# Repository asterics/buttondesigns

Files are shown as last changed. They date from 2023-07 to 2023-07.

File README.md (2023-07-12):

# Assistive Buttons

Depending on the use case and the abilities of a user, different button constructions might be useful.

In this folder, we share different button designs, which can be 3D printed.

## Arcade Buttons

These buttons are design around arcade buttons.

**Advantages:**
* Robust
* Cheap
* Easy to order

**Disadvantages:**
* Big button cases
* Relatively high actuation force necessary

**Use cases:**
* Spasticity
* No fine motor skills

**Necessary tools:**
* 3D Printer (or ordered 3D printed parts)
* Solder iron + solder
* Wirecutter
* (insulation stripping tool)

**Necessary parts:**
* 3D printed case
* 3.5mm stereo jack plug cable, jack to jack (you just need half of it for each button): [Example cable](https://www.aliexpress.com/item/4000208914309.html)
* Arcade button (24 or 30mm): [24mm](https://www.aliexpress.com/wholesale?SearchText=24mm+arcade+button) [30mm](https://www.aliexpress.com/wholesale?SearchText=24mm+arcade+button)

## Microswitches

We designed these switches for users with very low movements and little force to actuate buttons.
At Pollin, a German electronics distributor, we found ALPS keyboard switches with 0.3N actuation force, perfect for us!

In addition, the small case is designed to hold a 2.5mm² copper wire, which is used for flexible mounting of the button, as close
as possible to the user's fingers or toes.

**Advantages:**
* Very little force necessary
* Fast printing
* Flexible mounting
* Tiny

**Disadvantages:**
* Switches are more expensive
* Not that robust
* Switches are discontinued, but replacement is available

**Use cases:**
* Little movement possible
* Narrow space for button mounting
* Little actuation force necessary

**Necessary tools:**
* 3D printer (or ordered 3D printed parts)
* Solder iron + solder
* Wirecutter
* Hot glue gun + hot glue (or euqivalent glue, e.g. epoxy)

**Necessary parts:**
* 3D printed case
* 2.5mm²/AWG13 copper wire (~30cm/12") with insulation for mounting
* 3.5mm stereo jack plug cable, jack to jack (you just need half of it for each button): [Example cable](https://www.aliexpress.com/item/4000208914309.html)
* ALPS SPVF140100: [Pollin (Germany)](https://www.pollin.de/p/2-wege-eingabetaster-alps-spvf140100-420643) [Neuhold Elektronik (Austria)](https://www.neuhold-elektronik.at/catshop/product_info.php?products_id=4348) [Aliexpress](https://www.aliexpress.com/wholesale?SearchText=SPVF140100)

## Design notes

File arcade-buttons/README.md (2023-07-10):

These button designs are used for Arcade buttons. Depending on the ordered button diameter, please print either **button_24mm.stl** or **button_30mm.stl**.

Following parts are necessary (in addition to the 3D print):

* Arcade button (either 24mm or 30mm diameter)
* 3.5mm jack plug stereo audio cable (you can cut a plug-to-plug wire into half for 2 buttons)

After printing the case, you need to remove the built-in support material within the button.

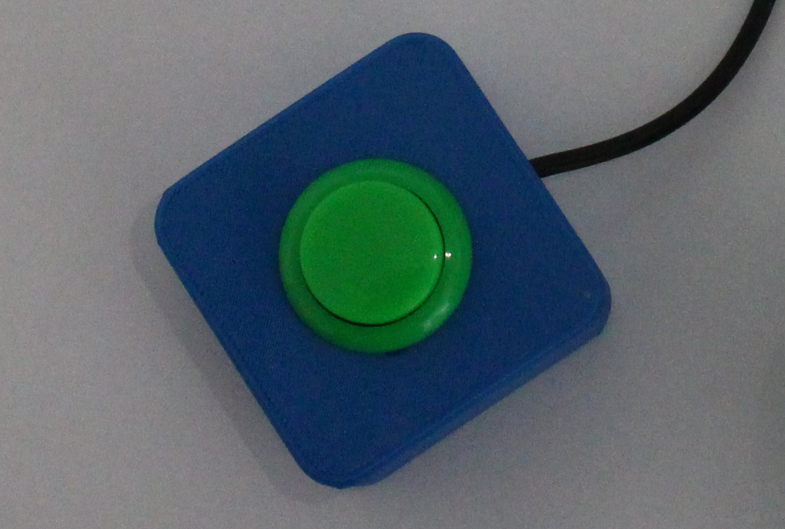
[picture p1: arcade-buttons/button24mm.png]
Image of a 24mm button

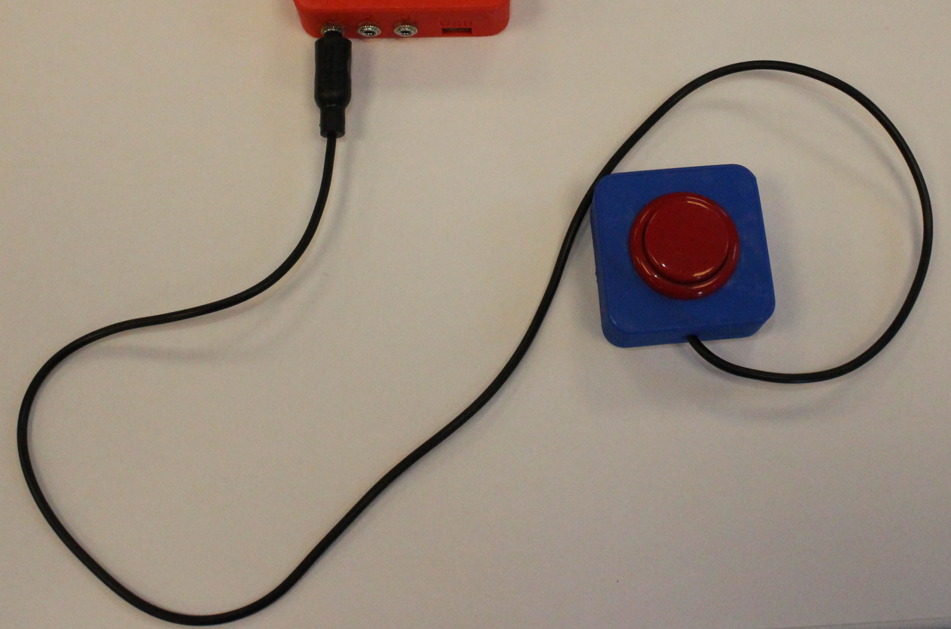
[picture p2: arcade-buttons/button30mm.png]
Image of a 30mm button


## Designfiles

Both button designs are located in __arcade_buttons.FCStd__ or __arcade_buttons_round.FCStd__ for the round case.

## Print settings & tools

All designs are made with FreeCAD v0.20.1.

Recommended print settings:

* 0.2-0.35mm
* Place the button hole on the printbed!
* No support
* Please use PLA or other biocompatible/-degradable filament (we use GreenTec from extrudr.at)

All designs are tested on a Prusa i3 MK3.

## Pictured construction manual

* [German](./ArcadeButton_DE.pdf?raw=true)
* [English](./ArcadeButton_EN.pdf?raw=true)

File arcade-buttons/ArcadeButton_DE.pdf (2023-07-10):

# Arcade Button – Bauanleitung

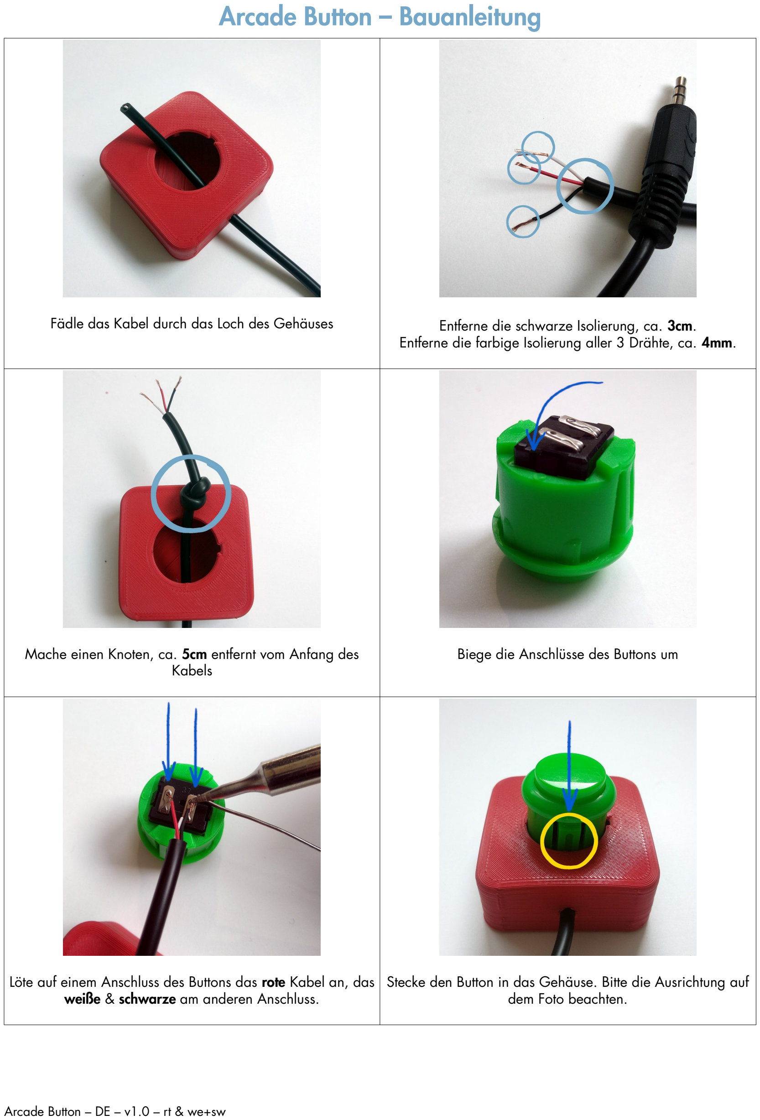
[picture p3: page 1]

Fädle das Kabel durch das Loch des Gehäuses | Entferne die schwarze Isolierung, ca. 3cm. Entferne die farbige Isolierung aller 3 Drähte, ca. 4mm.
Mache einen Knoten, ca. 5cm entfernt vom Anfang des Kabels | Biege die Anschlüsse des Buttons um
Löte auf einem Anschluss des Buttons das rote Kabel an, das weiße & schwarze am anderen Anschluss. | Stecke den Button in das Gehäuse. Bitte die Ausrichtung auf dem Foto beachten.

Arcade Button – DE – v1.0 – rt & we+sw

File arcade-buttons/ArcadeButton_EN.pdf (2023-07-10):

# Arcade Button – Construction Manual

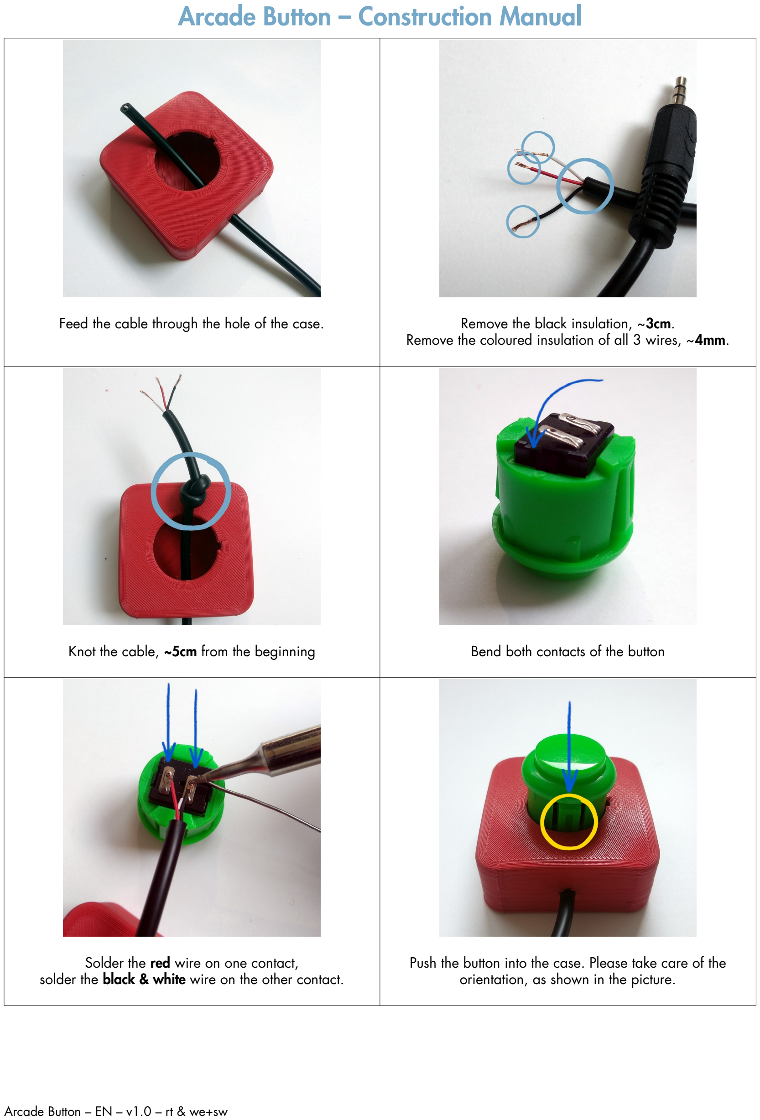
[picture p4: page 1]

Feed the cable through the hole of the case. | Remove the black insulation, ~3cm. Remove the coloured insulation of all 3 wires, ~4mm.
Knot the cable, ~5cm from the beginning | Bend both contacts of the button
Solder the red wire on one contact, solder the black & white wire on the other contact. | Push the button into the case. Please take care of the orientation, as shown in the picture.

Arcade Button – EN – v1.0 – rt & we+sw

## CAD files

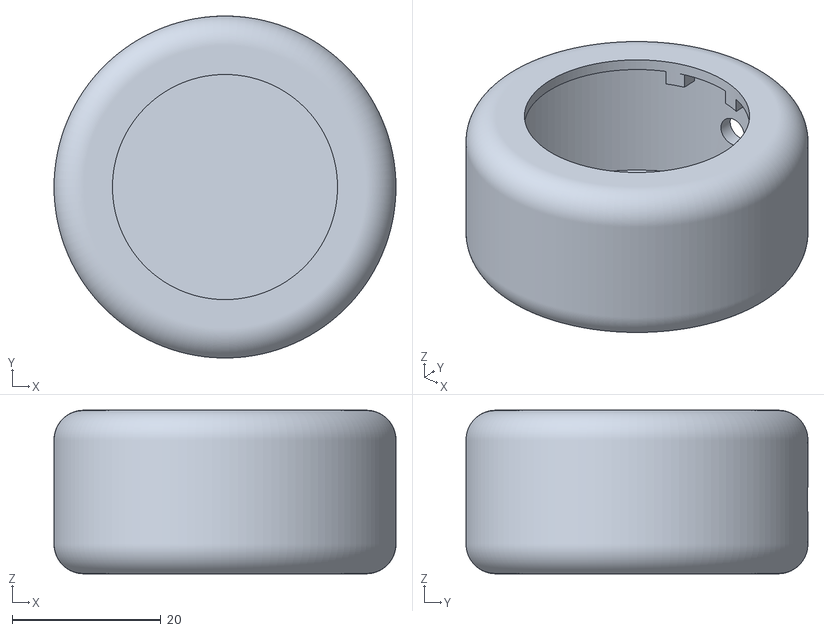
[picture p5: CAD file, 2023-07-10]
arcade-buttons/round_30mm.stl
46.0 x 46.0 x 22.0

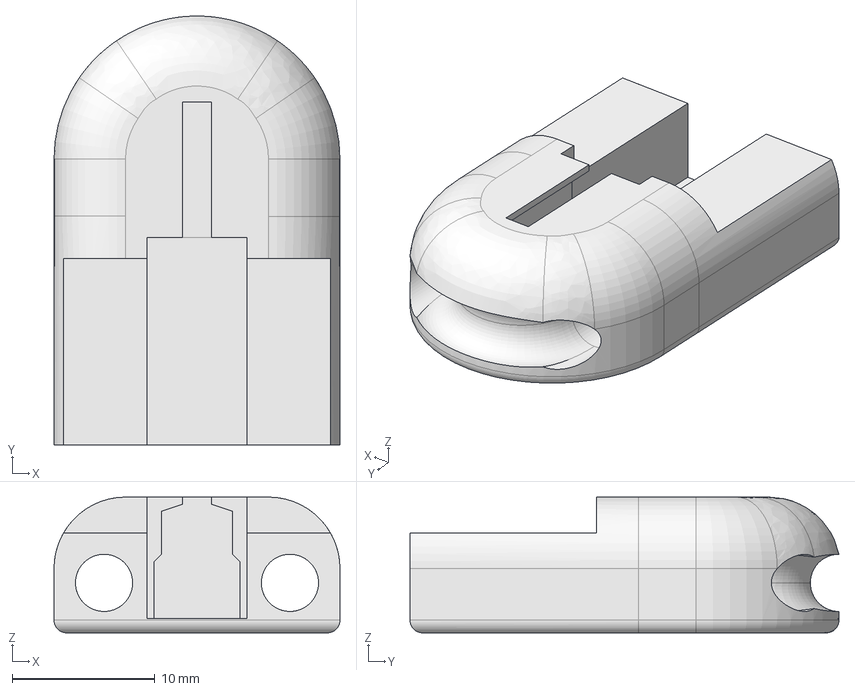
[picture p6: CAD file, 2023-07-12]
microswitch/ALPS_button.fcstd
20.0 x 30.0 x 9.50 mm

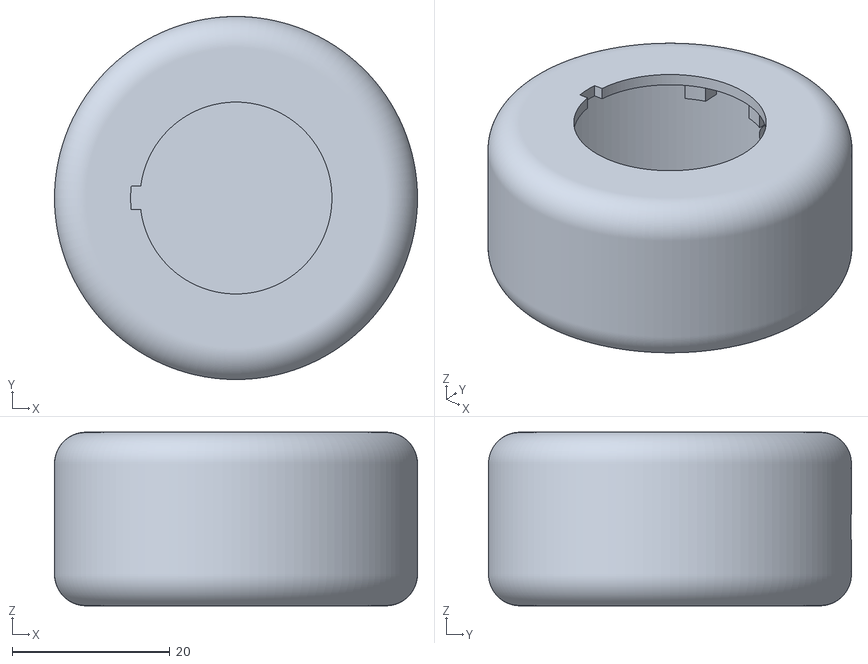
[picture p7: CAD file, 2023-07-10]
arcade-buttons/round_24mm.stl
46.0 x 46.0 x 22.0

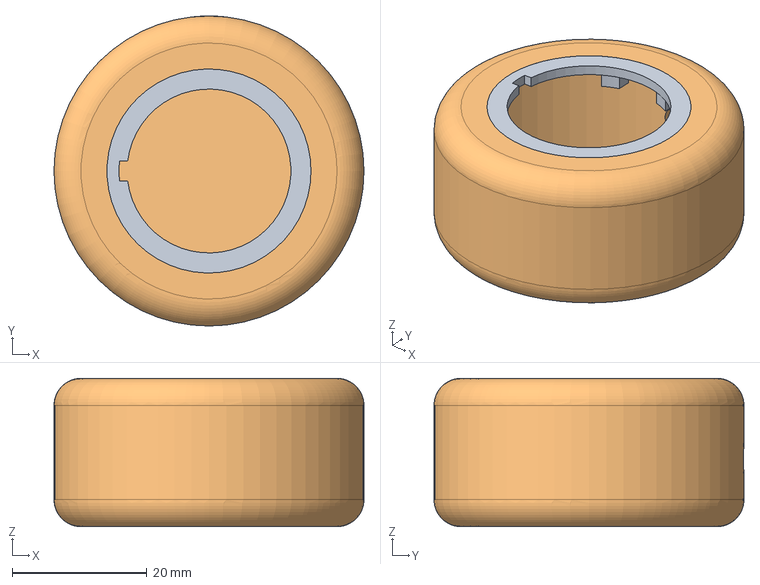
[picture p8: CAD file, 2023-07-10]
arcade-buttons/arcade_buttons_round.FCStd
46.0 x 46.0 x 22.0 mm
case_24mm
case_30mm

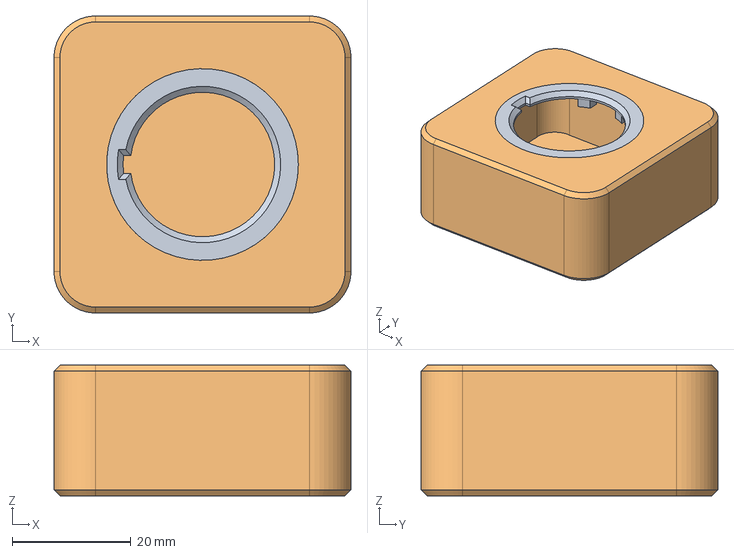
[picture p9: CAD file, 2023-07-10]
arcade-buttons/arcade_buttons.FCStd
50.0 x 50.0 x 22.0 mm
case_24mm
case_30mm

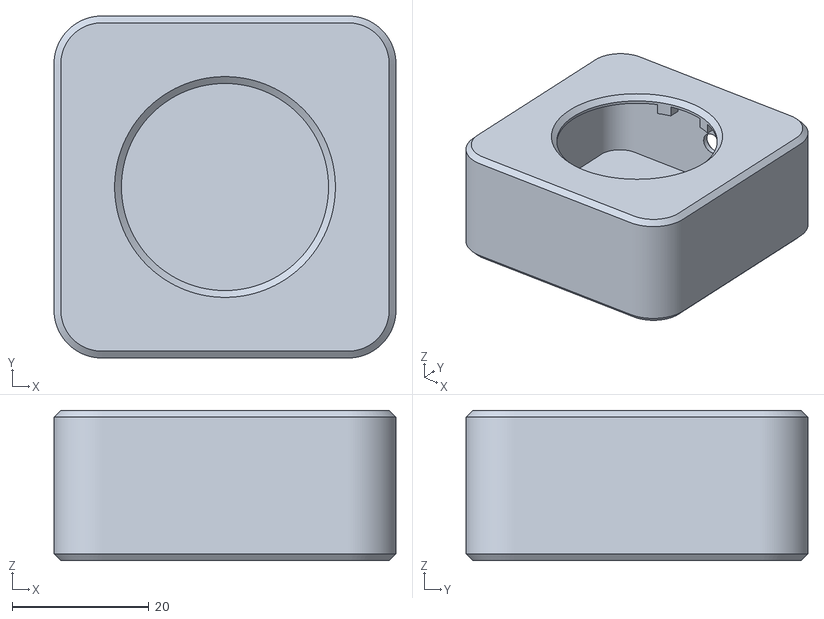
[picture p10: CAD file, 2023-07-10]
arcade-buttons/button_30mm.stl
50.0 x 50.0 x 22.0

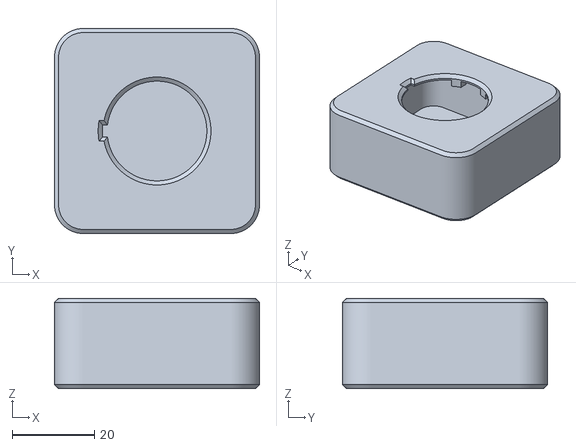
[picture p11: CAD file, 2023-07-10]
arcade-buttons/button_24mm.stl
50.0 x 50.0 x 22.0

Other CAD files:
microswitch/ALPS_button.stl

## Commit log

2023-07-10 Added 24/30mm Arcade button cases
    [arcade_buttons.FCStd, arcade_buttons_round.FCStd, button_24mm.stl, button_30mm.stl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]
2023-07-12 Added microswitch design
    [ALPS_button.fcstd, ALPS_button.stl]
